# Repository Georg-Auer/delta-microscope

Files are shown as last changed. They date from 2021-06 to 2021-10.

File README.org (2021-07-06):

* Low-cost, automated microscope stage
* PureData Version
*This page describes how to build an automated inverted 3d printed microscope for observing microfluidics chips.*

This is a [[https://www.plus.ac.at/biowissenschaften/der-fachbereich/arbeitsgruppen/lepperdinger/spoc-labs/][SPOC lab]] project. Original source code of the project
is provided under MIT License. The source may contain code under a different license, if this is the case it is stated in the LICENSE file.
*This page describes how to create a simple het cam robot.*

If not stated otherwise, the designs and documentation in this repository
are made publicly available under a
[[https://creativecommons.org/licenses/by/4.0/][Creative Commons Attribution 4.0 International (CC BY 4.0)]] License.

#+CAPTION: Image of the 3D-printed version of the microscope.
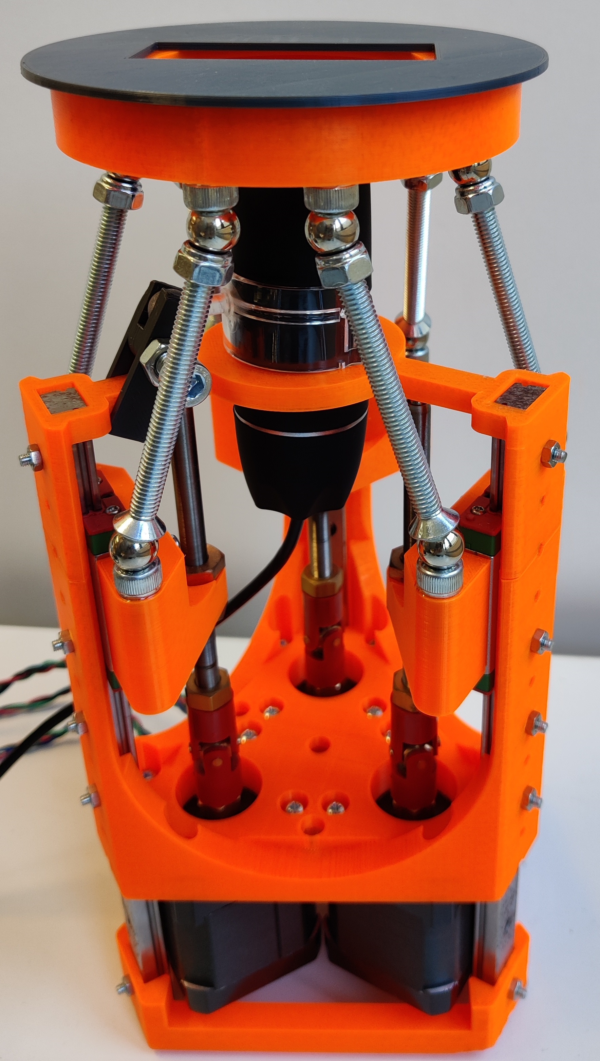
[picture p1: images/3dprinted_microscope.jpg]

#+BEGIN_QUOTE
Image of the 3D-printed microscope.
#+END_QUOTE

** Introduction

The microscope is designed to be as cheap and quick to manufacture as possible,
and still achieve high accuracy. Due to the chosen delta kinematics
the device has a very small footprint, and is also suitable for use in an incubator.
incubator. In the SPOC lab, the microscope is used
to observe and monitor the generation of spheroids in self-constructed chips and monitor the process.
The microscope can be controlled directly
or automated via a program to observe an experiment over time.

** Mechanics - Files and Bill of Materials   

*** Pump Design files (openSCAD)

The microscope model was designed in openSCAD in parametric form.
For each part, an stl file was created and all files where then sliced
with Prusa Slicer and sent to print on an 3D filament printer (Prusa MK3).
For the ease of reproduction of the slicer files are also saved within the directory.

#+CAPTION: A screenshot of the microscope in openSCAD.
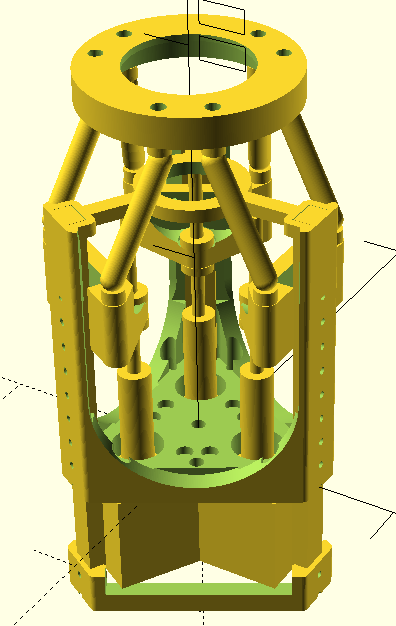
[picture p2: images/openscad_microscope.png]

#+BEGIN_QUOTE
A screenshot of the microscope in openSCAD (for the file see
[[./files/3d/openscad-microscope.scad]]).
#+END_QUOTE

*** Bill of Materials

| item                                                           | number | purpose               | bought from   |  part-no | costs in € |
|----------------------------------------------------------------+--------+-----------------------+---------------+----------+------------|
| Allegro A4983 Based Stepper Boards: here the 'Big Easy Driver' |      3 | stepper board         | Technobots    | 2900-445 | ~ 70       |
| Teensy 4.0 or 4.1 Microcontroller                              |      1 | stepper control       | Conrad        |  2269230 | ~ 30       |
| Nema 17 Steppers (0.9° 2.4 A)                                  |      3 | stepper motor         | Act-motor     | 1402-050 | ~ 60       |
| Fine Hex Adjuster, 1/4"-80, 4" Long                            |      3 | leadscrew             | Thorlabs      | F25SS400 | ~ 40       |
| Locking Phosphor-Bronze Bushing with Nut, 1/4"-80, L=0.50"     |      3 | leadscrewnut          | Thorlabs      |   N80L6P | ~ 28       |
| Linear Guide Rails (min 200 mm)                                |      3 | slides platform       | Amazon        | CNBTR214 | ~ 45       |
| Universal Coupling Body                                        |      3 | motor-screw-connector | Technobots    | 4604-050 | ~ 12       |
| Universal Coupling Insert - 5 mm                               |      3 | motor-side            | Technobots    | 4604-059 | ~ 8        |
| Universal Coupling Insert - 1/4"                               |      3 | screw-side            | Technobots    | 4604-066 | ~ 8        |
| OTHER SMALL ITEMS                                              |        |                       |               |          |            |
| 160 mm x 100 mm Copper Clad Stripboard                         |      1 | mount for electronics | Conrad        |          | ~ 2        |
| Male & Female PCB Headers 2.45 mm pitch                        |   some | simple connectors     | Conrad        |          | ~ 10       |
| Screws M3 (10 mm): 12 for motors, 6 for sliders, 15 for guides |     33 | mount slider & motors | Bauhaus       |          |            |
| Nuts M3                                                        |     33 | fixing screws         | Bauhaus       |          |            |
| Screws M6 (15 mm)                                              |     12 | suspension            | Bauhaus       |          |            |
| Screws M6 (60 mm)                                              |      6 | suspension            | Bauhaus       |          |            |
| Nuts M6 (end nut)                                              |      6 | suspension            | Bauhaus       |          |            |
| Neodymium bullet magnets ⌀ 10 mm                               |      6 | suspension            | Bauhaus       |          |            |
| USB (micro) cable                                              |      1 |                       | Conrad        |          | ~ 3        |
| 6 wire colored ribbon cable                                    |    3 m |                       | Conrad        |          | ~ 3        |
| 12 V / >=5 A power supply                                      |      1 |                       | Conrad        |          | ~ 20       |
| 197 g 3D-printer filament (PLA 1.75 mm)                        |1*250 g | microscope structure  | 3d jake       |          | ~ 10       |
| USA Digital Microscope 40x-1000x                               |      1 | microscope camera     | Bysameyee     |          | ~ 20       |
|----------------------------------------------------------------+--------+-----------------------+---------------+----------+------------|
|                                                                |        |                       |               |          | <  400     |

**** Companies:
- Technobots:  http://www.technobotsonline.com
- Thorlabs:    http:/www.thorlabs.com
- CPC-Farnell: http://cpc.farnell.com/
- RS:          http://uk.rs-online.com/web/
- Techsoft:    http://www.techsoft.co.uk/
- Maplin:      http://www.maplin.co.uk

All components but the optics-screws (Thorlabs) can be obtained
commercially. If other leadscrews are used, the software has to be
adapted to the distance/revolution grading.

**** Machines (and/or):
- FDM 3D-printer (we use an Prusa MK3, but any model with an similar precision would do)
#+EMAIL:  science@georgauer.com

#+CAPTION: Image of the 3D-printed version of robot.

#+BEGIN_QUOTE
Image of the robot.
#+END_QUOTE

** Introduction

Biocompatibility is of new untested materials is an important field.
This robot is a proposal of an automated het-cam experiment.

** TODO Mechanics - Files and Bill of Materials   

*** TODO  Design files

*** TODO Bill of Materials

- PLA
- stepper motor driver
- stepper motor
- arduino
- raspberry 4
- raspberry hq video camera

**** Machines (and/or):
- FDM 3D-printer (Prusa MK3, but any model with an similar precision would do)

**** Tools:
- Soldering iron
- Hand tools (screwdrivers etc.)

** Mechanical Assembly 

**** Pre-Assembly of Parts
***** Motor Part
- tin the leads of the motors with solder, add a male
  PCB-connector (or any other connector of your choosing. On our
  motors the colored leads are GREEN, BLACK, BLUE, RED).
- we use heatshrinking tube to electrically isolate the connectors at the end.
- add the connector for the leadscrew (5 mm brass insert) to the
  motor - you might not have space to do that later.

***** Leadscrew Part
- add the brass insert to connect the motor onto the leadscrew
- insert the screw VERY carefully to avoid damaging the thread which can
  happen rather easily.

***** Camera
The Microscope can be exchanged with an variety of solutions. We tried an Raspberry HQ Camera v1.0
with SM1 to C-mount adapter (thorlabs, SM1A9) to 1 inch optics connected to an Zeiss Plan 2,5 objective,
but eventually ended up with an 25€ USB microscope camera that has a 40x-1000x zoom option for maximal flexibility.

**** Assembly of the microscope

The STL files for the microscope where sliced in Prusa Slicer 2.2.0 and printed in ecoPLA NeonOrange with 20% infill.
The linear guide rails where screwed onto the main part, and the top part was then screwed onto the guide rails with 15xM3 screws and nuts.
For correct assembly, the top part has to end on height of the guide rails.
The three stepper motors where then screwed (12xM3) onto the bottom part.
The bottom part needs to be screwed on the other end of the guide rails (3xM3).
Now the universal couplings are screwed onto the motors and the optical fine threaded rods are fixed on the other side of the universal couplings.
For better durability, the plastic part of the universal couplings are glued to the metallic part with epoxy glue.
Six M6x15 mm screws are glued into the three slider parts, and M6x15 mm are glued into the platform as preparation for the magnetic joints.
The slider parts are now joined with their threaded insert and can be screwed onto the guide rails.
The end nuts are now placed on the M6 screws (60 mm) and the microscope stage is completed by putting the neodymium magnets in the joint positions.
Finally, the microscope-camera can be put in the ring on top where it is held in position with the printed clamp.

** Electronics
To drive the stepper motors we use a A4983 stepper driver
chip from Allegro Microsystems (datasheet http://www.technobotsonline.com/Datasheets2/1518-009-A4983SETTR-T.pdf).
For convenience we use one 'Big Easy Driver' for each motor
(http://www.technobotsonline.com/big-easy-driver.html,
http://www.schmalzhaus.com/BigEasyDriver/). The 'Big Easy Driver'
boards are nice, because they default to 16 step microstepping mode,
when the 'MS1, MS2, MS3' pins are left unconnected (which means that
less soldering has to be done). With 16-step microstepping, one
revelation of the leadscrew (318 micrometer movement) is divided into
400*16=6400 steps resulting in a stable flow even at very low
flowrates. The stepper drivers are controlled
with a teensy 4.0 or 4.1 microcontroller.

#+CAPTION: Left: Images of the electronics board with three stepper driver boards mounted. Right: Schematic diagram.

#+BEGIN_QUOTE
Left: Images of the electronics board with three stepper driver boards
mounted. Right: Schematic diagram.
#+END_QUOTE

*** Make the board
- solder connectors onto the driver board (e.g. PCB-connectors)

- layout the parts on a stripboard and drill holes so that you can
  mount the board with screws to an enclosure (e.g. from laser-cut
  acrylic).

- solder female PCB-connectors on the board for the teensy and the
  stepper boards (don't forget to cut the traces on the stripboard
  underneath).
- make all the necessary connections (see layout...)

- we made the system as simple as possible: 
  - no connection to MS1, MS2, MS3 - all are pulled high when not
    connected (means the driver defaults to 16 microstep-mode
  - no connection to sleep (slp) and reset (rst) - if powered the
    system will be on all the time. If you want to shut down the
    motors, turn off the power.
 
  - this leaves only the following connections to be made:
    - enable (en) is pulled low on all by connecting to ground (this
      is important, else the pins float).
    - shared GND between teensy and the quadstepper board (or single
      big easy drivers)
    - step-pin (stp): if high for >1 microsecond, the motor will step
    - direction-pin (dir): high/low sets the direction (if one of the motors
      steps the 'wrong' direction, just reverse the connections of the
      leads from (e.g. green, black, blue, red --> to red, blue,
      black, green).

  - Teensy is powered by a USB connection and the motors are powered
    separately (we use a 12V 5A power supply).

- Don't forget to adjust the current supplied to the motor with the
  small potentiometer on the stepper driver board. On max, the chip
  gets hot and the motor might have enough torque to continue beyond
  the end-stop, damaging the microscope assembly.

* Software for the Microscope
** Introduction - mode of operation and choice of tools

The microscope motors are controlled with a microcontroller (a 'teensy' 4.0 or 4.1)
and a software front end written in Pure Data (PD). The teensy
(https://www.pjrc.com/teensy/teensy31.html) is a 3.3V, 32-bit ARM
based microcontroller that is compatible with the Arduino toolchain
(https://www.arduino.cc/en/Guide/HomePage) and therefore easy to
program. The prime reason to use a teensy is the high speed USB data
transfer they allow
(https://www.pjrc.com/teensy/benchmark_usb_serial_receive.html). Apart
from controlling machinery, the teensy is well suited for data
acquisition tasks.

Pure Data (PD, https://puredata.info/) is an open source dataflow
programming language used primarily for music and video applications.
It runs on nearly every computing platform, is straightforward to
learn and can be modified 'live'.

The communication protocol between the microcontroller and PD is OSC
('Open Sound Control', https://www.opensoundcontrol.org). It is a very
flexible, easy to use two-way communication.

#+CAPTION: System diagram.

#+BEGIN_QUOTE
System diagram.
#+END_QUOTE

** Install the Software Toolchain
*** Arduino/Teensyduino
The easiest way to program teensy microcontrollers is to use the
Arduino IDE (download:https://www.arduino.cc/en/Main/Software). For
the teensy microcontrollers to be recognised by the Arduino IDE, one
must additionally install 'Teensyduino' (download:
https://www.pjrc.com/teensy/td_download.html). There is a detailed
tutorial on software installation and its use on the webpage. Most of
the Arduino libraries are compatible with teensy, Teensyduino itself
comes with many optimized ones (full install recommended).

** Setting up the System 
- program the teensy
- open the webpage

** How the System Works  
In the frontend control on the webpage, the rotation movement of the individual
of the individual motors is calculated.
This number of steps is now sent to the microcontroller,
which in turn controls the motor driver via the Step/Dir protocol.

** Getting it to Run
*** To get a debian system to run all necessary programs, use the new-raspi.sh shell script.

#+CAPTION: Screenshot of the program. 
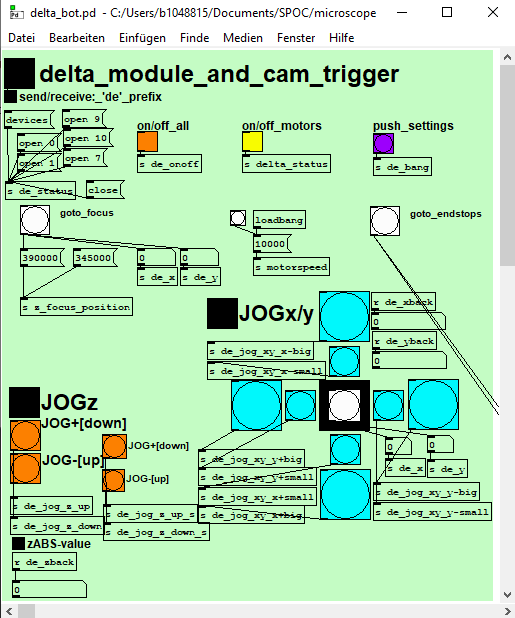
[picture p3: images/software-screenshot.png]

#+BEGIN_QUOTE
Screenshot of the program. 
#+END_QUOTE

- Hit [devices], and the available serial ports will show in the
  console window. One of them is connected to the teensy. Click [open
  x[ (change the numbers by entering editing mode, ctrl-e (linux),
  cmd-e (mac)) and PD should connect to the teensy.

- upload the corresponding file to the microcontroller
  ([[./files/delta_microscope_arduino/delta_microscope_arduino.ino]]).
- place the PD-programs ([[./files/delta_microscope/delta_microscope.pd]])
 together with a little helper-program for OSC ([[./files/o.io.slipserial.pd]]) in a folder and
  open it in PD-extended or PD-L2ORK.
- The file 'run.py' is the python/flask software.
- The files ([[./files/python/calibration.py]]) and ([[./files/frontend/delta_microscope_pd_osc_receiver.pd]])
  can be used together to calibrate the microscope.

#+CAPTION: Screenshot of the program. 
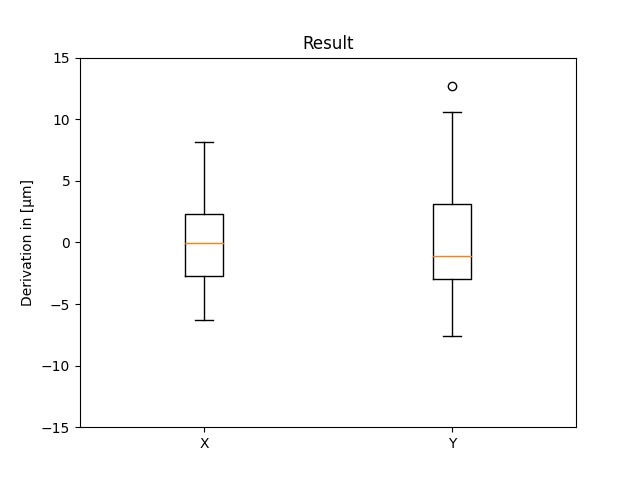
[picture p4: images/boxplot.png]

#+BEGIN_QUOTE
The microscope stage can now be controlled via an additional python script.
At first, an experiment to run to different x/y positions and back to the origin has to be created and executed.
After reaching the origin again, a picture of a raster is taken and saved in the experiment folder.

After running the experiment 25 times (n = 25), this resulting boxplot was calculated automatically with the calibration.py script.
#+END_QUOTE
** TODO Assembly

* Software for the Microscope
** TODO Introduction 

git clone --recurse-submodules git@github.com:spoc-lab/delta-microscope.git

pip install -r requirements.txt
for torch on armv7l:
https://github.com/Kashu7100/pytorch-armv7l

# install torch on Raspberry 3/4:
sudo apt install libopenblas-dev libblas-dev m4 cmake cython python3-dev python3-yaml python3-setuptools
cd ~/Downloads
git clone https://github.com/Kashu7100/pytorch-armv7l.git
cd pytorch-armv7l/
sudo pip3 install torch-1.7.0a0-cp37-cp37m-linux_armv7l.whl
sudo pip3 install torchvision-0.8.0a0+45f960c-cp37-cp37m-linux_armv7l.whl

# install on all systems:
sudo pip3 install -r requirements.txt

How to make the script run on startup:
sudo nano /etc/rc.local
insert:
cd home/pi/het-cam-dashboard
sudo CAMERA=opencv python3 run.py &

# git pull on startup
sudo nano ~/.profile
git --git-dir=/delta-microscope/.git pull main

or for additional logging:
sudo CAMERA=opencv python3 run.py & > /home/pi/Desktop/log.txt 2>&1

https://blog.miguelgrinberg.com/post/flask-video-streaming-revisited

to start an OpenCV session from bash, you can do this:

$ CAMERA=opencv python3 run.py

From a Windows command prompt you can do the same as follows:

on windows run:
$ python run.py CAMERA=opencv
$ py -3.7 run.py CAMERA=opencv

or:
$ set CAMERA=opencv
$ python run.py
$ py -3.7 run.py

or on linux with gunicorn:
# gunicorn -b 127.0.0.1:8080 app:app
# gunicorn -w 2 -b 127.0.0.1:8080 app:app

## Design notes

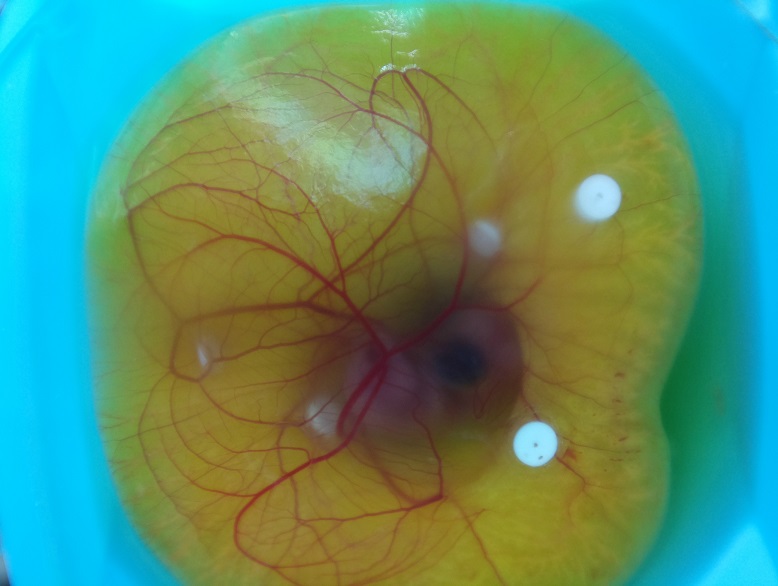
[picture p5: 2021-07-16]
het-cam-ha-small.jpg

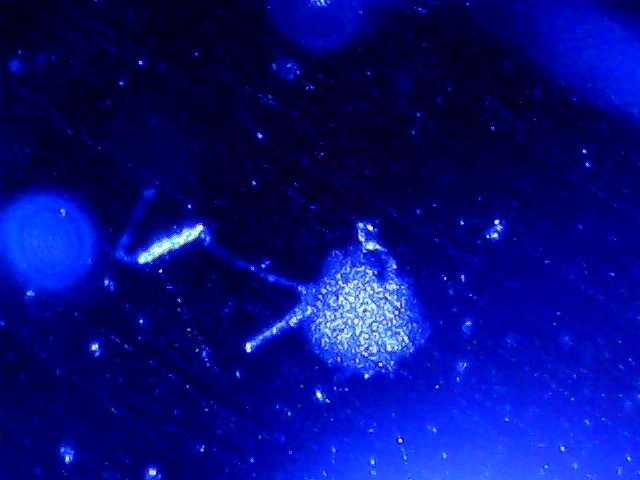
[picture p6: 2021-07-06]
spheroids1.jpg

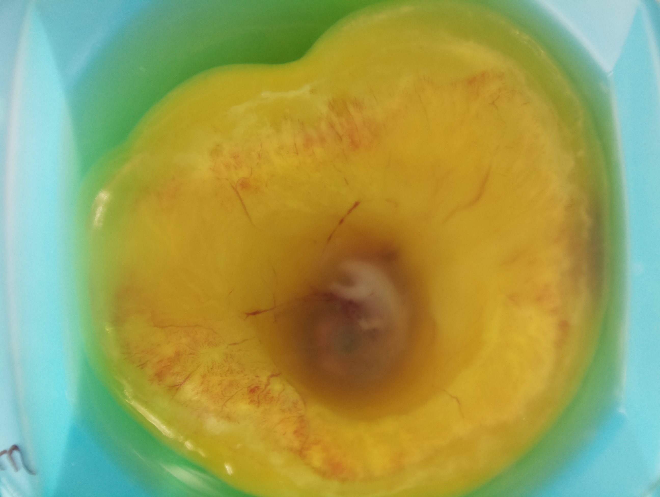
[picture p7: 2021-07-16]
het-cam-dead.jpg

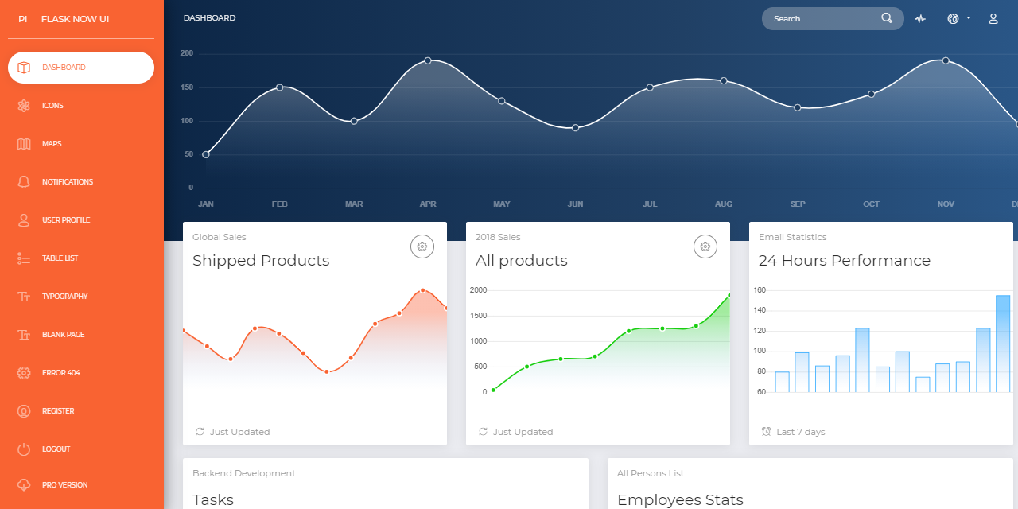
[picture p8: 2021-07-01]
media/flask-now-ui-dashboard-screen.png

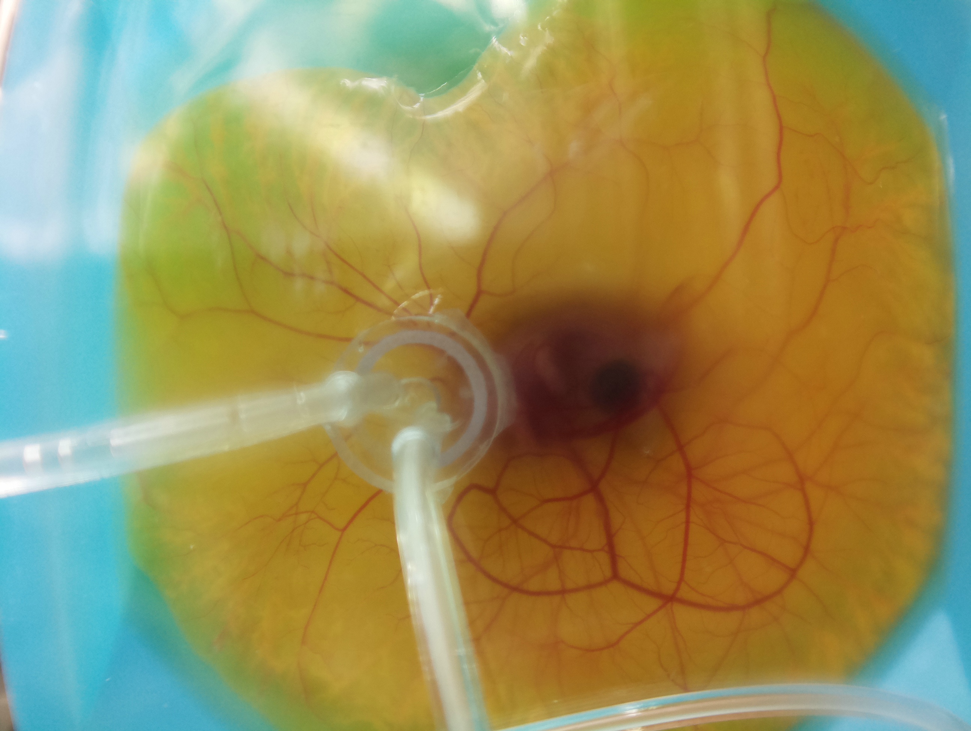
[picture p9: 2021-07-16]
het-cam.jpg

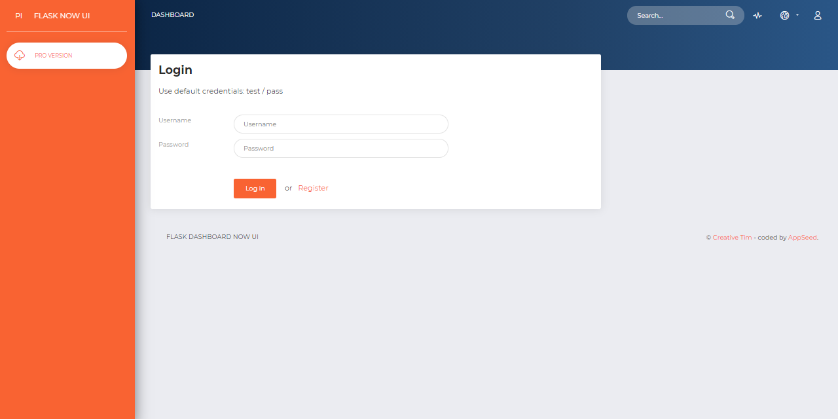
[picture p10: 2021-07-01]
media/flask-now-ui-dashboard-screen-login.png

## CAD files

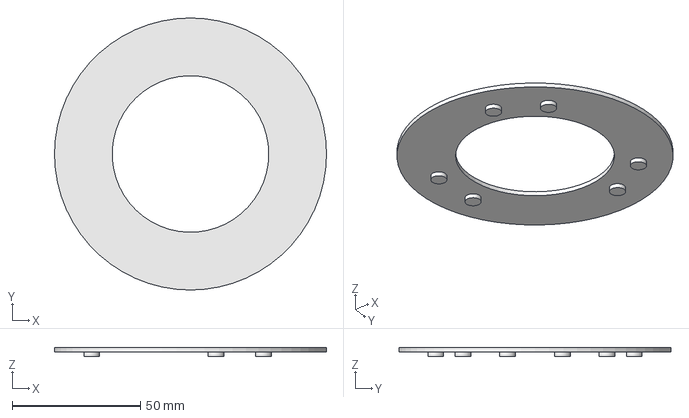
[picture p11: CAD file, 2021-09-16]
files/3d/accessories/complete_cutout_turntable_accessory.step
106.0 x 106.0 x 3.50 mm

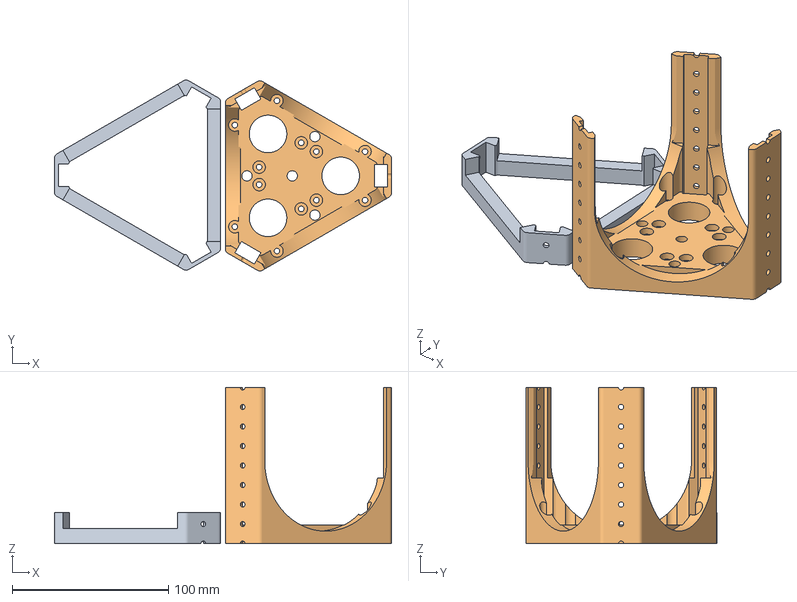
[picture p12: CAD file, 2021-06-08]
files/3d/mainparts_0.2mm_tolerance.3mf
215.7 x 122.3 x 100.0 mm
bottompart_delta_0.2mm_tolerance.stl
mainpart_delta_0.2mm_tolerance.stl

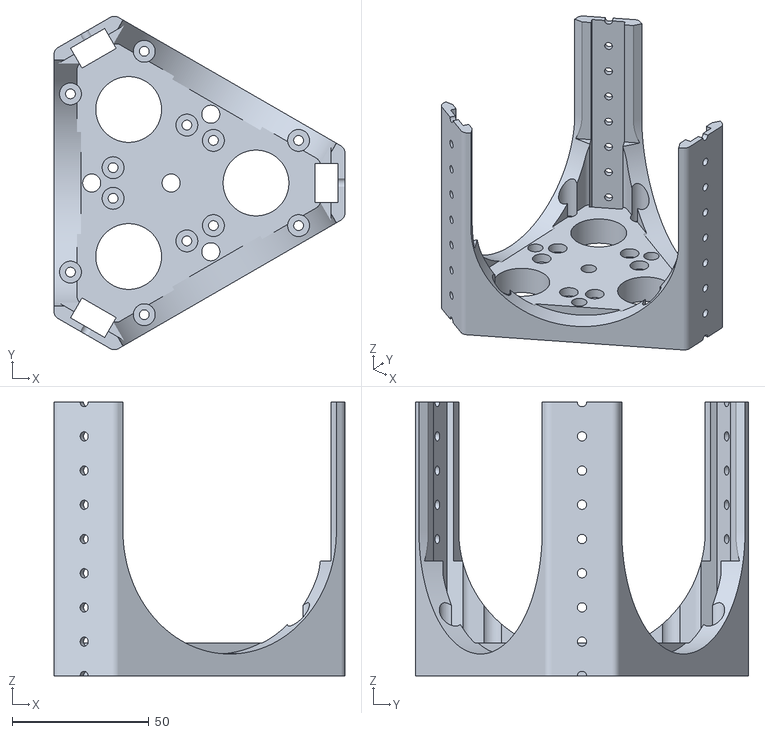
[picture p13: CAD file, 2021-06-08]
files/3d/mainpart_delta_0.2mm_tolerance.stl
106.3 x 121.8 x 100.0

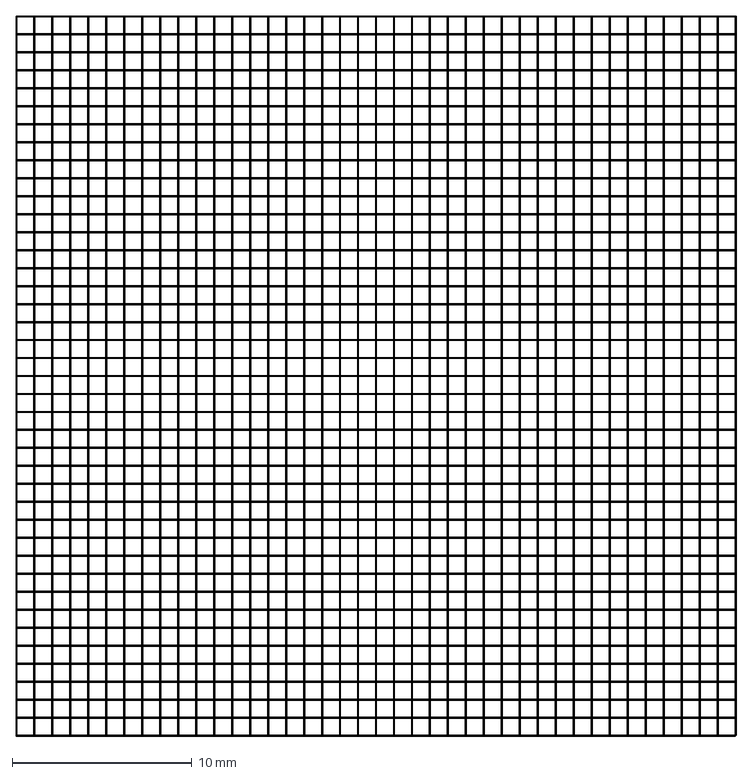
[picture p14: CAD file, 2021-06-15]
files/calibration/raster4x4.dxf
40.0 x 40.0 mm

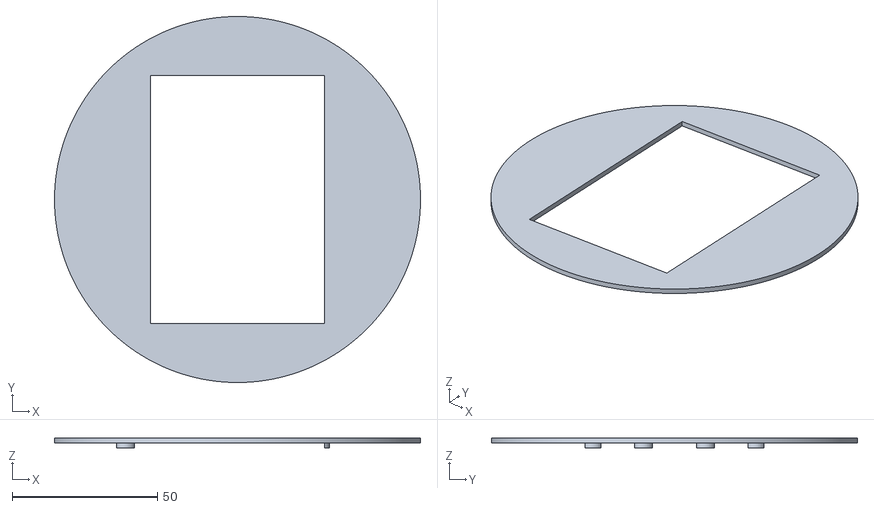
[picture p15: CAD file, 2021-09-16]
files/3d/accessories/modified_turntable_accessory_incubationchamber_85x59.4stl.stl
126.0 x 126.0 x 3.50

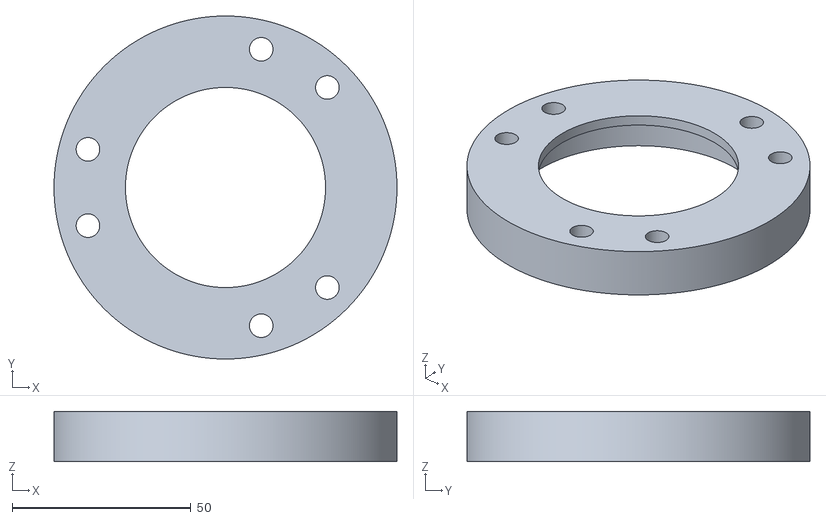
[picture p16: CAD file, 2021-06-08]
files/3d/platform_delta_0.2mm_tolerance.stl
96.0 x 96.0 x 14.0

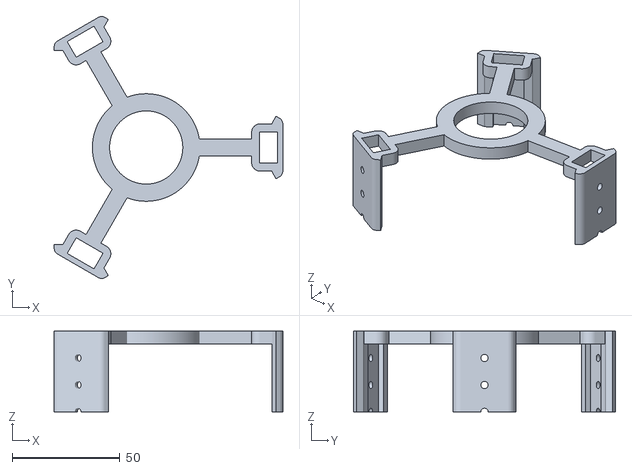
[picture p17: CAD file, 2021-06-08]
files/3d/toppart_delta_0.2mm_tolerance.stl
106.3 x 121.8 x 37.5

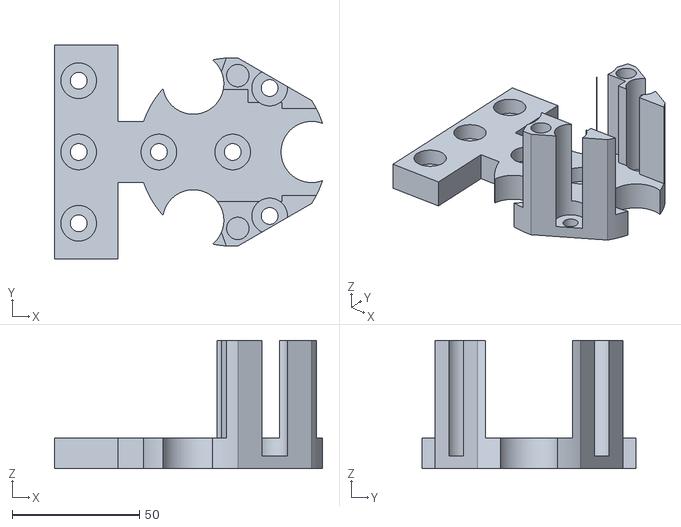
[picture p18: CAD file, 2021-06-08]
files/3d/optics_delta_0.2mm_tolerance.stl
105.3 x 84.0 x 50.3

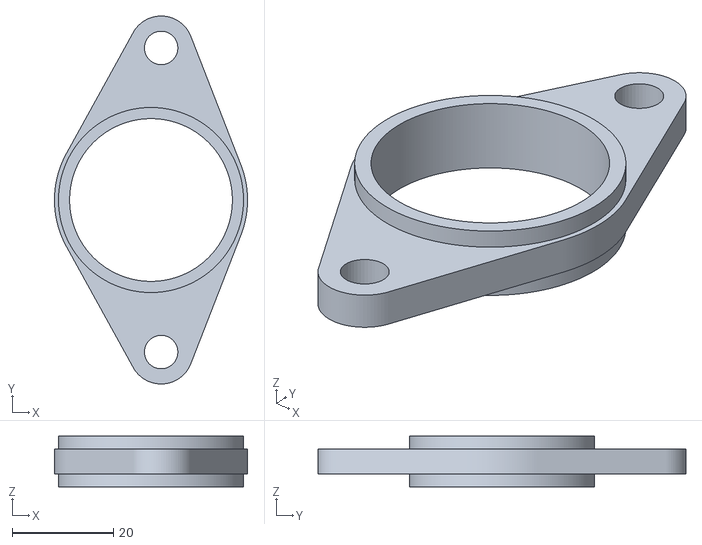
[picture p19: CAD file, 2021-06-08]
files/3d/optics_fixture_delta_0.2mm_tolerance.stl
38.1 x 72.6 x 10.0

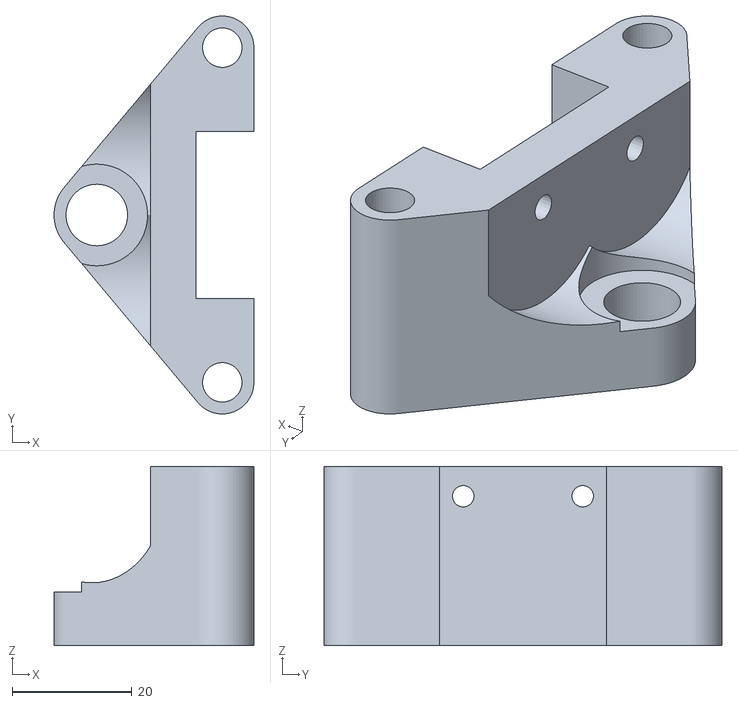
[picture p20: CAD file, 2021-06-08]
files/3d/slider_x3_delta_0.2mm_tolerance.stl
33.4 x 66.6 x 30.0

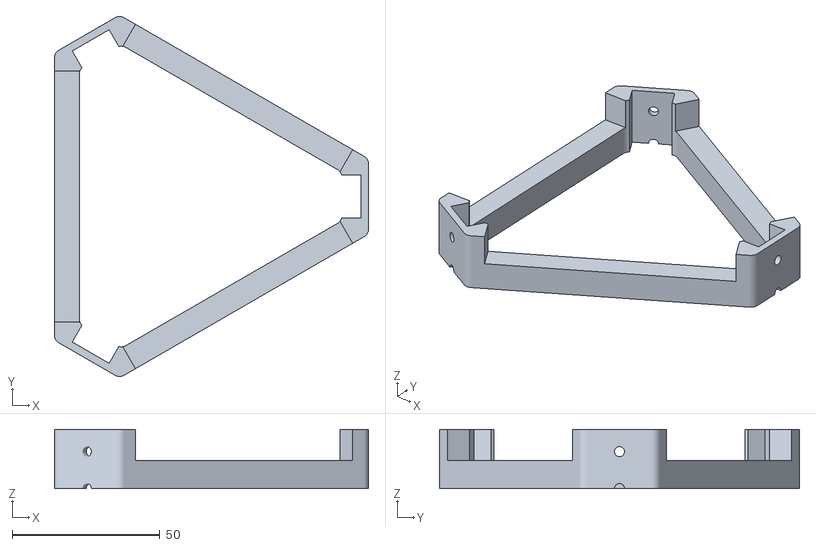
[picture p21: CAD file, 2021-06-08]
files/3d/bottompart_delta_0.2mm_tolerance.stl
106.3 x 121.8 x 20.0

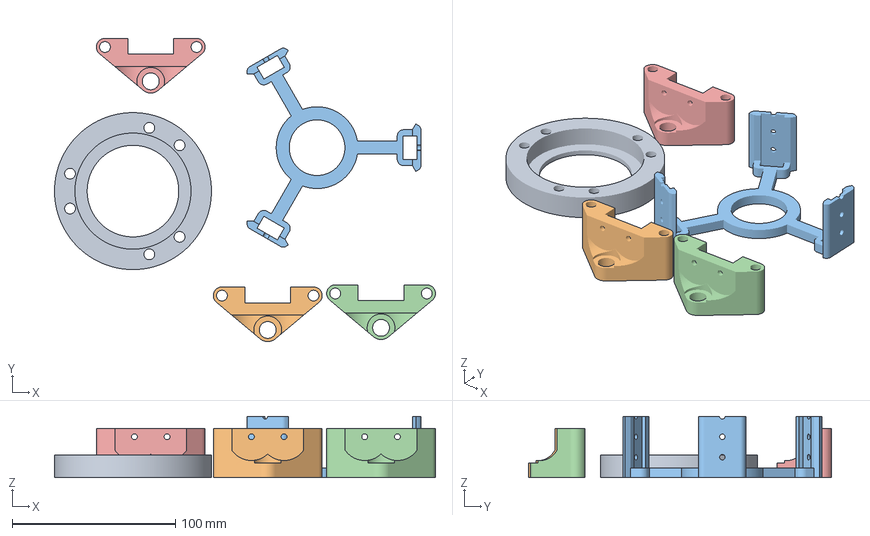
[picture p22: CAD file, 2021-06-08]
files/3d/small_parts_0.2mm_tolerance.3mf
233.0 x 185.5 x 37.5 mm
platform_delta_0.2mm_tolerance.stl
slider_x3_delta_0.2mm_tolerance.stl x 3
toppart_delta_0.2mm_tolerance.stl

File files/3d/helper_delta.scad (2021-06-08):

//mini nema17-based delta
//printable on 120x120x120 trinus - max size possible
//and pumps to mount onto the scaffold
//===================================================

tolerance=0.2; //added tolerance at places needed to make 3d-printed part fit

//==================
//variables baseunit
//==================
base_r=31;//this is where the center-motorhole is located from abs center; adjusts size in xy; 31=min for nema17; this keeps all 'inside features' while making it easy to adjust outside wall via 'movewallfrombase_r'
movewallfrombase_r=29.5; //this variable moves the outside wall further from base_r (center motor holes)
height_all=100; //=height of delta-part
platethickness=12;//thickness of baseplate
reinforcementheight=30;//height above plate where hiwin-carriage is not cut out from wall
edge_y_distance=22; //distance of cylinders to form hull (inside-wall=edge_y_distance-wallthickness); use this variable to adjust wall behind sliders
wallthickness=9;//thickness of wall (grows to the inside)
edge_r=3;//'roundness' of edges
//M6 centerholes made so that hex-head is embedded
M6baseholes_r=3.3; //size of hole in center
M6_sinking_depth=7;//depth of access holes for M6 screws so that hex-head or nut is fully sunk
M6baseholeaccess_r=7;

motor_screw_diagonal = 44;//to mount nema17's 
middlemotor_r = 12; //radius of middle 'hole' of motors, big enough for 3d-printed couplers
M3_r=1.8;//a bit r added for not too tight holes to mount motors
motorscrews_access_r=4; //access_r for motor screws
motorscrews_access_heightbelowbaseplate=4; //how deep access holes go into baseplate
//subtract cylindrical shape from walls
//------------------------------------
cylinder_dia=45;
cylinder_length=100; //just that it easy to hit the wall for subtraction
wallheight_hole=-4;//mm above bottomplate where cylindrical cutout starts
cutout_r=33;//where from center cutout in wall will start
///variables hiwin
//----------------
M4_r=1.7; //r for screws, unfortunately imperial, therefore M3 screws must be used
M4_distance=12.5; //distance mounting holes, twice as many holes than in slider (25mm distance)
M4length=22; //length of screws
slide_width=14;//hiwin-slide=12mm +2mm space on each side
slide_thickness=8;//thickness hiwin-slide

slide_length=200;//length of hiwin-slides
move_slide_from_Zzero=-62.5; //move slider + screws above/below z-zero
slider_distance=22; //additional distance of slider from 'base-radius' base_r; take care if motors interfere
hiwin_carrierheight=5; //height of slider vs rail of hiwin from above
hiwin_carrier_width=28; //width of hiwin carrier (27mm+1)      
hiwin_carrier_thickness=10; //   

//===============
//variables TOP-Deltapart
//===============
delta_toplength=60;
delta_topwidth=20;
delta_topthickness=6;
delta_top_hole_r=17;
delta_top_wallthickness=8;

//=====================
//variables for slider
//=====================
height_slider = 80;//this defines where (height above plate) carriage is 
sliderwall=2;//thickness of wall around vertical holes
sliderpart_z_height=30;//height in z     
magnetdistance_to_sides=56; //USE THIS TO MAXIMISE MOVEMENT POSSIBLE + s_holder_r_in & s_holder_M6_r
magnetdistance_from_base_r=21; //distance in x from base_r to magnets   
M6_r=3.3; //+0.3 for 3d-printing

M6magnet_cutout_dia=6;//can put magnets lower, now commented out
M6magnet_cutout_height=7;//can put magnets lower, now commented out


bolt_distance_carrier=20; //distance holes on hiwin slider
carrier_screwlength=20;
screw_lengthinplastic=8;
sliderscrewaccess_r=3;
sliderscrewaccess_r_top=14.5;//r of cutout on top-screws connected on hiwin carrier

leadscrewnut_accessdia = 8.5; //leadscrewnut-nuts r=7.5 'leadscrewnut_top_bottom_r'

//========================
//variables for base plate
//========================
height_all_bottompart=20; //=height of delta-bottom_part
wallheight_hole_bottompart=5;//mm above bottomplate where cylindrical cutout starts
cylinder_dia_bottompart=60;
bottompart_base_correction=-8;//arbitrary value to adjust height of connection piece

//=======================================
//variables for drawing mechanical parts
//=======================================
//draw motors
motor_length = 48;
motor_width = 42;
motor_halfdiagonal = 0.5* sqrt(2*(motor_width*motor_width)); //half the diagonal of square area of motor, could be too big when edges of motor are rounded
//draw shafts, coupler, leadscrew and leadscrewnut
shaftcoupler_length = 52;//the usual red one
shaftcoupler_radius = 7.5;//the usual red one

leadscrew_length = 130; //~4" +approx height of shaft-coupler=42
leadscrew_radius = 3.05;
//dimensions thorlabs-nut
leadscrewnut_length = 9;
leadscrewnut_minradius = 5.15; //dia real = 9.5, 0.3mm tolerance added for 3d-printing
leadscrewnut_top_bottom_r=7.5;
leadscrewnut_top_bottom_thickness=4;
//=====================================

//==========================
//variables optics parts
//==========================

//point grey fireflyMV camera
//===========================
//main body
ptgrey_x=44;
ptgrey_y=34;
ptgrey_z=19.18;
//USB-port
ptgrey_x_USB=10; //check with caliper
ptgrey_y_USB=15; //check with caliper
ptgrey_z_USB=5.2;
//IO-port
ptgrey_x_IO=15; //check with caliper
ptgrey_y_IO=5; //check with caliper
ptgrey_z_IO=2; //too much, but like this easy to see...
IO_from_left_edge=33.49;
IO_from_top_edge=7.56;
//============================


//30mm-thorlabs-cage (e.g. mirror)
//================================
cageoptics_xy=38.3+2*tolerance;
cageoptics_z=38.3;
itemonside_xy=12;
itemonside_thickness=5+tolerance;
itemonfront_thickness=20;//takes away space for 1inch optics
itemonfront_width=34;//takes away space for 1inch optics  

//thorlabs c->1" adapter
c_to_1inch_adapter_r_outer=15.35;
c_to_1inch_adapter_r_inner=11.45;
c_to_1inch_adapter_height=4.4; 
// 1" optics tubes
tube1inch_outer_r=15.25;
tube1inch_inner_r=11.45;
// tube1
t1_tube1inch_length=80;
//tube2
t2_tube1inch_length=25.4;
//10xolympus_objective
olympus10x_parfocal_length=45.06;
olympus10x_parfocal_r=0.5;
olympus10x_body1_r=12; 
olympus10x_bodylength1=28;
olympus10x_body2_r=8;
olympus10x_bodylength2=32;
olympus10x_body3_r=5.25;
olympus10x_bodylength3=34;
//==============================
//variables optics ground plate
//=============================
//round part
optics_plate_r=37;//adjust this to fit well inside deltapart
optics_plate_z=12; //z-height of plate
optics_plate_z_high=optics_plate_z+cageoptics_z; //z-height of middle part
opticsplate_fixhole_r=29;

//brass-inserts to mount fixture
 M6insert_r=4.4;//4.5 good for holes across layers, but too big when holes are in other printing direction
 M6insert_height=14; //min 13.5mm
 insert_x=2;
 insert_y=30;
//connector-part to outside
optics_addpart1_x=15;//must be larger than wall-end of deltapart
optics_addpart1_y=24;//must fit to size of corresponding cylinder-cutout from deltapart 
optics_addpart_movex=30;//moves connector part in x, make it fit to the optics plate in delta
//outside part which serves to screw on bigger outside platform
optics_addpart2_x=25;
optics_addpart2_y=84;  

//=============================
//optics-plate - fixture on top
//=============================
opticsfixture_height=5;
opticsfixture_wallsize=3;
//====================
//optics ADDED plate
//====================
opticsaddedplate_x=87.5;
opticsaddedplate_y=112.5;  
holestepsize=12.5;


//==================================
//PLATFORM (slide-holder)-variables
//==================================
s_holder_height=14;
s_holder_r_out=48;
// MAX MOVEMENT ADJUSTMENT: s_holder_r_in & s_holder_M6_r & magnetdistance_to_sides
s_holder_r_in=35.5;//ADJUST THIS TO MAXIMISE MOVEMENT "when the objective crushes into platform" 
//to find best place for screws and the dimensions of the place iterate manually until both ECHO messages (or green and yellow inner circles match and are at max
s_holder_M6_r=28.5; //ADJUST THIS TO MAXIMISE MOVEMENT "where the hex-screws are" 
s_holder_FOV_r_outside=base_r+magnetdistance_from_base_r-s_holder_M6_r; //base for ECHO: diameter of movement possible from outside structure (one side: rods vertical)
s_holder_FOV_r_inside=s_holder_r_in-olympus10x_body1_r; //base for ECHO: diameter of movement possible from inside structure (ring and objective) 

s_holder_r_top=28;  //s_holder_r_in; //only needed to differ from s_holder_r_in if uscope slide is to small... 
s_holder_r_top_height=3;//holding structure smaller than air-gap between objective and sample

//carriage-platform connectors
//============================   
     magnet_r=5;//neodymium sphere radius
     hex_r=4.95;//hex-head_r 
     hex_height=5.85;//hex-head height
     magnet_in_hex_height=9.9;//measure this: when magnet is assembled in hex, where is its center, if hexhead-'bottom' = 0?
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

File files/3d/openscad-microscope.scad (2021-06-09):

//mini nema17-based delta
//printable on 120x120x120 trinus - max size possible
//and pumps to mount onto the scaffold
//===================================================

tolerance=0.2; //added tolerance at places needed to make 3d-printed part fit

//==================
//variables baseunit
//==================
base_r=31;//this is where the center-motorhole is located from abs center; adjusts size in xy; 31=min for nema17; this keeps all 'inside features' while making it easy to adjust outside wall via 'movewallfrombase_r'
movewallfrombase_r=29.5; //this variable moves the outside wall further from base_r (center motor holes)
height_all=100; //=height of delta-part
platethickness=12;//thickness of baseplate
reinforcementheight=30;//height above plate where hiwin-carriage is not cut out from wall
edge_y_distance=22; //distance of cylinders to form hull (inside-wall=edge_y_distance-wallthickness); use this variable to adjust wall behind sliders
wallthickness=9;//thickness of wall (grows to the inside)
edge_r=3;//'roundness' of edges
//M6 centerholes made so that hex-head is embedded
M6baseholes_r=3.3; //size of hole in center
M6_sinking_depth=7;//depth of access holes for M6 screws so that hex-head or nut is fully sunk
M6baseholeaccess_r=7;

motor_screw_diagonal = 44;//to mount nema17's 
middlemotor_r = 12; //radius of middle 'hole' of motors, big enough for 3d-printed couplers
M3_r=1.8;//a bit r added for not too tight holes to mount motors
motorscrews_access_r=4; //access_r for motor screws
motorscrews_access_heightbelowbaseplate=4; //how deep access holes go into baseplate
//subtract cylindrical shape from walls
//------------------------------------
cylinder_dia=45;
cylinder_length=100; //just that it easy to hit the wall for subtraction
wallheight_hole=-4;//mm above bottomplate where cylindrical cutout starts
cutout_r=33;//where from center cutout in wall will start
///variables hiwin
//----------------
M4_r=1.7; //r for screws, unfortunately imperial, therefore M3 screws must be used
M4_distance=12.5; //distance mounting holes, twice as many holes than in slider (25mm distance)
M4length=22; //length of screws
slide_width=14;//hiwin-slide=12mm +2mm space on each side
slide_thickness=8;//thickness hiwin-slide

slide_length=200;//length of hiwin-slides
move_slide_from_Zzero=-62.5; //move slider + screws above/below z-zero
slider_distance=22; //additional distance of slider from 'base-radius' base_r; take care if motors interfere
hiwin_carrierheight=5; //height of slider vs rail of hiwin from above
hiwin_carrier_width=28; //width of hiwin carrier (27mm+1)      
hiwin_carrier_thickness=10; //   

//===============
//variables TOP-Deltapart
//===============
delta_toplength=60;
delta_topwidth=20;
delta_topthickness=6;
delta_top_hole_r=17;
delta_top_wallthickness=8;

//=====================
//variables for slider
//=====================
height_slider = 80;//this defines where (height above plate) carriage is 
sliderwall=2;//thickness of wall around vertical holes
sliderpart_z_height=30;//height in z     
magnetdistance_to_sides=56; //USE THIS TO MAXIMISE MOVEMENT POSSIBLE + s_holder_r_in & s_holder_M6_r
magnetdistance_from_base_r=21; //distance in x from base_r to magnets   
M6_r=3.3; //+0.3 for 3d-printing

M6magnet_cutout_dia=6;//can put magnets lower, now commented out
M6magnet_cutout_height=7;//can put magnets lower, now commented out


bolt_distance_carrier=20; //distance holes on hiwin slider
carrier_screwlength=20;
screw_lengthinplastic=8;
sliderscrewaccess_r=3;
sliderscrewaccess_r_top=14.5;//r of cutout on top-screws connected on hiwin carrier

leadscrewnut_accessdia = 8.5; //leadscrewnut-nuts r=7.5 'leadscrewnut_top_bottom_r'

//========================
//variables for base plate
//========================
height_all_bottompart=20; //=height of delta-bottom_part
wallheight_hole_bottompart=5;//mm above bottomplate where cylindrical cutout starts
cylinder_dia_bottompart=60;
bottompart_base_correction=-8;//arbitrary value to adjust height of connection piece

//=======================================
//variables for drawing mechanical parts
//=======================================
//draw motors
motor_length = 48;
motor_width = 42;
motor_halfdiagonal = 0.5* sqrt(2*(motor_width*motor_width)); //half the diagonal of square area of motor, could be too big when edges of motor are rounded
//draw shafts, coupler, leadscrew and leadscrewnut
shaftcoupler_length = 52;//the usual red one
shaftcoupler_radius = 7.5;//the usual red one

leadscrew_length = 130; //~4" +approx height of shaft-coupler=42
leadscrew_radius = 3.05;
//dimensions thorlabs-nut
leadscrewnut_length = 9;
leadscrewnut_minradius = 5.15; //dia real = 9.5, 0.3mm tolerance added for 3d-printing
leadscrewnut_top_bottom_r=7.5;
leadscrewnut_top_bottom_thickness=4;
//=====================================

//==========================
//variables optics parts
//==========================

//point grey fireflyMV camera
//===========================
//main body
ptgrey_x=44;
ptgrey_y=34;
ptgrey_z=19.18;
//USB-port
ptgrey_x_USB=10; //check with caliper
ptgrey_y_USB=15; //check with caliper
ptgrey_z_USB=5.2;
//IO-port
ptgrey_x_IO=15; //check with caliper
ptgrey_y_IO=5; //check with caliper
ptgrey_z_IO=2; //too much, but like this easy to see...
IO_from_left_edge=33.49;
IO_from_top_edge=7.56;
//============================


//30mm-thorlabs-cage (e.g. mirror)
//================================
cageoptics_xy=38.3+2*tolerance;
cageoptics_z=38.3;
itemonside_xy=12;
itemonside_thickness=5+tolerance;
itemonfront_thickness=20;//takes away space for 1inch optics
itemonfront_width=34;//takes away space for 1inch optics  

//thorlabs c->1" adapter
c_to_1inch_adapter_r_outer=15.35;
c_to_1inch_adapter_r_inner=11.45;
c_to_1inch_adapter_height=4.4; 
// 1" optics tubes
tube1inch_outer_r=15.25;
tube1inch_inner_r=11.45;
// tube1
t1_tube1inch_length=80;
//tube2
t2_tube1inch_length=25.4;
//10xolympus_objective
olympus10x_parfocal_length=45.06;
olympus10x_parfocal_r=0.5;
olympus10x_body1_r=12; 
olympus10x_bodylength1=28;
olympus10x_body2_r=8;
olympus10x_bodylength2=32;
olympus10x_body3_r=5.25;
olympus10x_bodylength3=34;
//==============================
//variables optics ground plate
//=============================
//round part
optics_plate_r=37;//adjust this to fit well inside deltapart
optics_plate_z=12; //z-height of plate
optics_plate_z_high=optics_plate_z+cageoptics_z; //z-height of middle part
opticsplate_fixhole_r=29;

//brass-inserts to mount fixture
 M6insert_r=4.4;//4.5 good for holes across layers, but too big when holes are in other printing direction
 M6insert_height=14; //min 13.5mm
 insert_x=2;
 insert_y=30;
//connector-part to outside
optics_addpart1_x=15;//must be larger than wall-end of deltapart
optics_addpart1_y=24;//must fit to size of corresponding cylinder-cutout from deltapart 
optics_addpart_movex=30;//moves connector part in x, make it fit to the optics plate in delta
//outside part which serves to screw on bigger outside platform
optics_addpart2_x=25;
optics_addpart2_y=84;  

//=============================
//optics-plate - fixture on top
//=============================
opticsfixture_height=5;
opticsfixture_wallsize=3;
//====================
//optics ADDED plate
//====================
opticsaddedplate_x=87.5;
opticsaddedplate_y=112.5;  
holestepsize=12.5;


//==================================
//PLATFORM (slide-holder)-variables
//==================================
s_holder_height=14;
s_holder_r_out=48;
// MAX MOVEMENT ADJUSTMENT: s_holder_r_in & s_holder_M6_r & magnetdistance_to_sides
s_holder_r_in=35.5;//ADJUST THIS TO MAXIMISE MOVEMENT "when the objective crushes into platform" 
//to find best place for screws and the dimensions of the place iterate manually until both ECHO messages (or green and yellow inner circles match and are at max
s_holder_M6_r=28.5; //ADJUST THIS TO MAXIMISE MOVEMENT "where the hex-screws are" 
s_holder_FOV_r_outside=base_r+magnetdistance_from_base_r-s_holder_M6_r; //base for ECHO: diameter of movement possible from outside structure (one side: rods vertical)
s_holder_FOV_r_inside=s_holder_r_in-olympus10x_body1_r; //base for ECHO: diameter of movement possible from inside structure (ring and objective) 

s_holder_r_top=28;  //s_holder_r_in; //only needed to differ from s_holder_r_in if uscope slide is to small... 
s_holder_r_top_height=3;//holding structure smaller than air-gap between objective and sample

//carriage-platform connectors
//============================   
     magnet_r=5;//neodymium sphere radius
     hex_r=4.95;//hex-head_r 
     hex_height=5.85;//hex-head height
     magnet_in_hex_height=9.9;//measure this: when magnet is assembled in hex, where is its center, if hexhead-'bottom' = 0?
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

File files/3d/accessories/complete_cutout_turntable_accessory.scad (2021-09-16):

magnetdistance_to_sides=56; //USE THIS TO MAXIMISE MOVEMENT POSSIBLE + s_holder_r_in & s_holder_M6_r
magnetdistance_from_base_r=21; //distance in x from base_r to magnets   
M6_r=3.3; //+0.3 for 3d-printing

M6magnet_cutout_dia=6;//can put magnets lower, now commented out
M6magnet_cutout_height=7;//can put magnets lower, now commented out

s_holder_r_top=28;  //s_holder_r_in; //only needed to differ from s_holder_r_in if uscope slide is to small... 
s_holder_r_top_height=3;//holding structure smaller than air-gap between objective and sample

s_holder_height=14;
s_holder_r_out=48;
// MAX MOVEMENT ADJUSTMENT: s_holder_r_in & s_holder_M6_r & magnetdistance_to_sides
s_holder_r_in=35.5;//ADJUST THIS TO MAXIMISE MOVEMENT "when the objective crushes into platform" 
//to find best place for screws and the dimensions of the place iterate manually until both ECHO messages (or green and yellow inner circles match and are at max
s_holder_M6_r=28.5; //ADJUST THIS TO MAXIMISE MOVEMENT "where the hex-screws are" 

/*
//make cylindical platform
difference (){
cylinder(r = s_holder_r_out, h = s_holder_height, $fa=1, $fs=0.5);
cylinder(r = s_holder_r_in, h = s_holder_height-s_holder_r_top_height, $fa=1, $fs=0.5);
cylinder(r = s_holder_r_top, h = s_holder_height, $fa=1, $fs=0.5);  

for(turn0 = [0 : 120 : 360])
rotate([0,0,turn0]){
//attachment M6+magnets    
translate ([s_holder_M6_r, -magnetdistance_to_sides/2,0])  
cylinder(r = M6_r, h = s_holder_height, $fa=1, $fs=0.5);
translate ([s_holder_M6_r, magnetdistance_to_sides/2,0])  
cylinder(r = M6_r, h = s_holder_height, $fa=1, $fs=0.5);
}
}

*/

//tolerance due to fff printing method
tolerance = 0.2;
slide_tolerance = 0.1;

//to avoid the need for supports during printing:
slide_holder_overhang = 5;

//size of an typical slide
single_slide_lenght_1 = 76+tolerance;
single_slide_lenght_2 = 75+tolerance;
single_slide_width_1 = 26+tolerance;
single_slide_width_2 = 25+tolerance;

ring_widening = 5;

//create slide holding platform
color("red"){
translate ([0,0,20]){
difference(){

union(){



for(turn0 = [0 : 120 : 360])
rotate([0,0,turn0]){
//attachment poles    
translate ([s_holder_M6_r, -magnetdistance_to_sides/2,0])
cylinder(r = M6_r-tolerance, h = s_holder_height/8, $fa=1, $fs=0.5);
translate ([s_holder_M6_r, magnetdistance_to_sides/2,0])  
cylinder(r = M6_r-tolerance, h = s_holder_height/8, $fa=1, $fs=0.5);
}
translate ([0,0,s_holder_height/8])

//platform
difference(){
cylinder(r = s_holder_r_out+ring_widening, h = s_holder_height/8, $fa=1, $fs=0.5);
cylinder(r = s_holder_r_in, h = s_holder_height-s_holder_r_top_height, $fa=1, $fs=0.5);
cylinder(r = s_holder_r_top, h = s_holder_height, $fa=1, $fs=0.5);




}
}//end of union

// single slide frame
rotate([0,0,15]){
cube(size = [single_slide_lenght_1,single_slide_width_1,s_holder_height], center = true);
}
rotate([0,0,-15]){
cube(size = [single_slide_lenght_2,single_slide_width_2,s_holder_height], center = true);
}
// double slide frame
cube(size = [single_slide_width_1*2+slide_tolerance,single_slide_lenght_1+slide_tolerance,s_holder_height], center = true);
}
}
}

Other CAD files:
files/3d/accessories/modified_turntable_accessory_incubationchamber.scad
files/3d/accessories/complete_cutout_turntable_accessory.stl

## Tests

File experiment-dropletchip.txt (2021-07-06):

[0, 0, 0]
[100000, -50000, 0]
[20000, -170000, -40000]
[-100000, -110000, -40000]
[-160000, -220000, -110000]
[-40000, -270000, -110000]
[-120000, -360000, -150000]
[-280000, -390000, -180000]
[-170000, -430000, -180000]
[-230000, -500000, -210000]
[-330000, -450000, -210000]
[-360000, -510000, -220000]
[-410000, -560000, -240000]
[-320000, -600000, -240000]

'0,0,0\r\n100000, -50000, 0\r\n20000, -170000, -40000\r\n-100000, -110000, -40000\r\n-160000, -220000, -110000\r\n-40000, -270000, -110000\r\n-120000, -360000, -150000\r\n-280000, -390000, -180000\r\n-170000, -430000, -180000\r\n-230000, -500000, -210000\r\n-330000, -450000, -210000\r\n-360000, -510000, -220000\r\n-410000, -560000, -240000\r\n-320000, -600000, -240000'

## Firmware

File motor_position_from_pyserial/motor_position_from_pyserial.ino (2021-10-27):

#include <AccelStepper.h>
// https://www.pjrc.com/teensy/td_libs_AccelStepper.html
//configure AccelStepper to mode 1 (Step/Dir)
int board1 = 1;
//define Pins
int motor0_en = 1;
int motor0_dir = 2;
int motor0_step = 3;

int motor1_en = 4;
int motor1_dir = 5;
int motor1_step = 6;

int motor2_en = 7;
int motor2_dir = 8;
int motor2_step = 9;

int motor3_en = 10;
int motor3_dir = 11;
int motor3_step = 12;

//define Pins on AccelStepper library
AccelStepper motor0(board1, motor0_step, motor0_dir);
AccelStepper motor1(board1, motor1_step, motor1_dir);
AccelStepper motor2(board1, motor2_step, motor2_dir);
AccelStepper motor3(board1, motor3_step, motor3_dir);//...(1[means driver board], step, dir)

struct STRUCT {
  int motor0_enable = 1;
  int motor0_direction;
  int motor0_position;
  int motor0_speed = 5000;
  int motor1_enable = 1;
  int motor1_direction;
  int motor1_position;
  int motor1_speed = 5000;
  int motor2_enable = 1;
  int motor2_direction;
  int motor2_position;
  int motor2_speed = 5000;
  int motor3_enable = 1;
  int motor3_direction;
  int motor3_position;
  int motor3_speed = 5000;
} testStruct;

#include "SerialTransfer.h"

int ledPin = 13;     // pin that the led is attached to
//int analogvalue = 0;
int32_t arduino_motorA = 0;
int32_t arduino_motorB = 0;
int32_t arduino_motorC = 0;

int calculate_motorA(int32_t x_movement, int32_t y_movement, int32_t z_movement){
  //calculate arduino_motor A,B,C here
  int delta_arms = 1214550;  // L=60.12mm 1step = 0.0495um =1214550 ticks
  //int delta_radius = ????;
  int Ax0 = 408178; //=Bx0
  int Ay0 = 235663; //=By0
  arduino_motorA = (sqrt((pow(delta_arms,2))-(pow((Ax0+x_movement),2))-(pow((Ay0+y_movement),2))))-z_movement-0.5; //-0.5 to round down!
  int start_value = 1119367;
  arduino_motorA = arduino_motorA-start_value;
  return (arduino_motorA);
}
int calculate_motorB(int32_t x_movement, int32_t y_movement, int32_t z_movement){
  //calculate arduino_motor A,B,C here
  int delta_arms = 1214550;  // L=60.12mm 1step = 0.0495um =1214550 ticks
  //int delta_radius = ????;
  int Ax0 = 408178; //=Bx0
  int Ay0 = 235663; //=By0
  arduino_motorB = (sqrt(pow(delta_arms,2)-(pow((Ax0-x_movement),2))-(pow((Ay0+y_movement),2))))-z_movement-0.5; //-0.5 to round down!
  int start_value = 1119367;
  arduino_motorB = arduino_motorB-start_value;
  return (arduino_motorB);
}
int calculate_motorC(int32_t x_movement, int32_t y_movement, int32_t z_movement){
  //calculate arduino_motor A,B,C here
  int delta_arms = 1214550;  // L=60.12mm 1step = 0.0495um =1214550 ticks
  //int delta_radius = ????;
  int Cy0 = 471323;
  arduino_motorC = (sqrt((pow(delta_arms,2))-(pow(x_movement,2))-(pow((Cy0-y_movement),2))))-z_movement-0.5; //-0.5 to round down!
  int start_value = 1119368;
  arduino_motorC = arduino_motorC-start_value;
  return (arduino_motorC);
}
SerialTransfer myTransfer;

void setup()  
  {       
  
  //TODO: enable/disable motors from python
  
  //enable motors
  pinMode (motor0_en, OUTPUT); //motor0_EN
  pinMode (motor1_en, OUTPUT); //motor1_EN
  pinMode (motor2_en, OUTPUT); //motor2_EN
  pinMode (motor3_en, OUTPUT); //motor3_EN
  //motors on/off
  digitalWrite (motor0_en, HIGH); //motor0 HIGH:off, LOW:on
  digitalWrite (motor1_en, HIGH); //motor1
  digitalWrite (motor2_en, HIGH); //motor2
  digitalWrite (motor3_en, HIGH); //motor3
  
  motor0.setMaxSpeed(20000);  //always necessary, default very slow
  motor1.setMaxSpeed(20000); 
  motor2.setMaxSpeed(20000);
  motor3.setMaxSpeed(20000); 
  
  Serial.begin(115200);
  myTransfer.begin(Serial);

  //for testing purposes
  pinMode(ledPin, OUTPUT);  //set switch as input pin for rawdata-mode
  digitalWrite (ledPin, LOW);
}

void loop()  
{

  if(myTransfer.available())
  {
    // find size of transferred message
    uint16_t recSize = 0;
    recSize = myTransfer.rxObj(testStruct, recSize);
    
    // do the enable here, otherwise the stop condition and the motorX_en interfere
    digitalWrite (motor0_en, testStruct.motor0_enable); //motor0
    digitalWrite (motor1_en, testStruct.motor1_enable); //motor1
    digitalWrite (motor2_en, testStruct.motor2_enable); //motor2
    digitalWrite (motor3_en, testStruct.motor3_enable); //motor3

    //delta mechanics calculation
    arduino_motorA = calculate_motorA(testStruct.motor0_position,testStruct.motor1_position,testStruct.motor2_position);
    arduino_motorB = calculate_motorB(testStruct.motor0_position,testStruct.motor1_position,testStruct.motor2_position);
    arduino_motorC = calculate_motorC(testStruct.motor0_position,testStruct.motor1_position,testStruct.motor2_position);
    
    // send all received data back to Python
    for(uint16_t i=0; i < myTransfer.bytesRead; i++)
      myTransfer.packet.txBuff[i] = myTransfer.packet.rxBuff[i];
    
    myTransfer.sendData(myTransfer.bytesRead);
  }

  // motor0.moveTo(testStruct.motor0_position);
  // motor1.moveTo(testStruct.motor1_position);
  // motor2.moveTo(testStruct.motor2_position);
  // motor3.moveTo(testStruct.motor3_position);

  motor0.moveTo(arduino_motorA);
  motor1.moveTo(arduino_motorB);
  motor2.moveTo(arduino_motorC);
  // motor3.moveTo(testStruct.motor3_position);

  motor0.setSpeed(testStruct.motor0_speed);
  motor1.setSpeed(testStruct.motor1_speed);
  motor2.setSpeed(testStruct.motor2_speed);
  motor3.setSpeed(testStruct.motor3_speed);

  motor0.runSpeedToPosition();  
  motor1.runSpeedToPosition();
  motor2.runSpeedToPosition();
  motor3.runSpeedToPosition();

// since the mechanics from each motor has a slight influence to all others
// the motors are only switched off if all movement is completed
// and every momentum (forward or backlash) is expected to be 0
  // if (motor0.distanceToGo()== 0 && motor1.distanceToGo()== 0 && motor2.distanceToGo()== 0 && motor3.distanceToGo()== 0){
  //   delay(300);
  //   digitalWrite (motor0_en, HIGH); //motor0
  //   testStruct.motor0_enable = 1; // turn motors off after distanceToGo is 0 for all motors
  //   digitalWrite (motor1_en, HIGH); //motor1
  //   testStruct.motor1_enable = 1;
  //   digitalWrite (motor2_en, HIGH); //motor2
  //   testStruct.motor2_enable = 1;
  //   digitalWrite (motor3_en, HIGH); //motor3
  //   testStruct.motor3_enable = 1;
  // }

  if (motor0.distanceToGo()== 0){
    // delay(500);
    digitalWrite (motor0_en, HIGH); //motor0
    testStruct.motor0_enable = 1; // turn motor off after distanceToGo is 0
  }
  if (motor1.distanceToGo()== 0){
    // delay(500);
    digitalWrite (motor1_en, HIGH); //motor1
    testStruct.motor1_enable = 1;
  }
  if (motor2.distanceToGo()== 0){
    // delay(500);
    digitalWrite (motor2_en, HIGH); //motor2
    testStruct.motor2_enable = 1;
  }
  if (motor3.distanceToGo()== 0){
    digitalWrite (motor3_en, HIGH); //motor3
    testStruct.motor3_enable = 1;
  } 
}  

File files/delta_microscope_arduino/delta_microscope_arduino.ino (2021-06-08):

//quadstepper_inverted deltabot

// kinematics integrated, 
// after movement finished, 
// cam and LED is triggered with time-settings specified in the OSC-message
// enable/disable motors

//xyz movement

//pins:
/*
-STANDARD WIRING DIAGRAM (teensy 3.x): not all pins are used in every setup!
=================================================================== 
    
* Modular Setup - PIN connections - teensy 3.2/3.6 compatible

| PIN | PUMP           | Pump-function  | DELTA-BOT      | SOLENOIDS | Sol-driver | MEASUREMENT/SORTING     | M/S function                                                             |
|-----+----------------+----------------+----------------+-----------+------------+-------------------------+--------------------------------------------------------------------------|
|   0 |                |                |                | SOL1      | ULN1/Pin1  |                         |                                                                          |
|   1 | enablePumppin  | EnableP0       | ENMD1          | SOL2      | ULN1/Pin2  |                         |                                                                          |
|   2 | directionpin   | DIRpump0       | MD1            | SOL3      | ULN1/Pin3  |                         |                                                                          |
|   3 | steppin        | STEPpump0      | MD1            | SOL4      | ULN1/Pin4  |                         |                                                                          |
|   4 | enablePump1pin | EnableP1       | ENMD2          | SOL5      | ULN1/Pin5  |                         |                                                                          |
|   5 | directionpin1  | DIRpump1       | MD2            | SOL6      | ULN1/Pin6  |                         |                                                                          |
|   6 | steppin1       | STEPpump1      | MD2            | SOL7      | ULN1/Pin7  |                         |                                                                          |
|   7 | enablePump2pin | EnableP2       | ENMD3          | SOL8      | ULN1/Pin8  |                         |                                                                          |
|   8 | directionpin2  | DIRpump2       | MD3            |           |            |                         |                                                                          |
|   9 | steppin2       | STEPpump2      | MD3            |           |            |                         |                                                                          |
|  10 | enablePump3pin | EnableP3       | not used       |           |            |                         |                                                                          |
|  11 | directionpin3  | DIRpump3       | not used       |           |            |                         |                                                                          |
|  12 | steppin3       | STEPpump3      | not used       |           |            |                         |                                                                          |
|-----+----------------+----------------+----------------+-----------+------------+-------------------------+--------------------------------------------------------------------------|
|  13 | not used       | not used       | not used       | SOL16     | ULN2/Pin8  |                         |                                                                          |
|  14 | A0 (not used)  | Trigger (opt)  | A0=cam-trigger | SOL15     | ULN2/Pin7  |                         |                                                                          |
|  15 | A1 (not used)  | Trigger (opt)  | A1=LED-trigger | SOL14     | ULN2/Pin6  |                         |                                                                          |
|  16 | endStopFpin    | EndSTOPP0Front | ESTOPMD1F      | SOL13     | ULN2/Pin5  |                         |                                                                          |
|  17 | endStopBpin    | EndSTOPP0Back  | ESTOPMD1B      | SOL12     | ULN2/Pin4  |                         |                                                                          |
|  18 | endStop1Fpin   | EndSTOPP1Front | ESTOPMD2F      | SOL11     | ULN2/Pin3  | Trigger3                | broken out with GND                                                      |
|  19 | endStop1Bpin   | EndSTOPP1Back  | ESTOPMD2B      | SOL10     | ULN2/Pin2  | Trigger2                | broken out with GND                                                      |
|  20 | endStop2Fpin   | EndSTOPP2Front | ESTOPMD3F      | SOL9      | ULN2/Pin1  | Trigger1                | broken out with GND                                                      |
|  21 | endStop2Bpin   | EndSTOPP2Back  | ESTOPMD3B      |           |            | CAMERA-Trigger          | broken out with GND                                                      |
|  22 | endStop3Fpin   | EndSTOPP3Front | not used       |           |            | LED-Strobe-Trigger      | broken out with GND                                                      |
|  23 | endStop3Bpin   | EndSTOPP3Back  | not used       |           |            | SENSOR-Measurement (A9) | with Analog-GND + 3.3V (talos-sensors); A-GND only (BNC-connected sens.) |
|     |                |                |                |           |            |                         |                                                                          |



camera-trigger: pin 14
LED-trigger: pin 15


motor1 (towerA, MD1)
enable              1
DIR                 2
STP                 3

motor2 (towerB, MD2)
enable              4
DIR                 5
STP                 6

motor3 (towerC, MD3)
enable              7
DIR                 8
STP                 9


Big Easy Driver - things not used:
/////////////////////////////////////////////////////////////////////////////////////
MS1 MS2 MS3  (16 ustepping per default)
H   H   H    1/16
/////////////////////////////////////////////////////////////////////////////////////

FORMAT OF THE OSC_MESSAGE
/////////////////////////
position/speed motors; 
camera-waiting time after movement completed (usec); 
3x(strobepulse & duration - in usec after camera was triggered); 
CAM&LED-on/off 

17 values:
==========

in_motorA
speed_motorA
in_motorB
speed_motorB
in_motorC
speed_motorC

delta_status
*/

// Library for stepper motors
#include <AccelStepper.h>

//define Pins
AccelStepper motorA(1, 3, 2);
AccelStepper motorB(1, 6, 5);
AccelStepper motorC(1, 9, 8);//...(1[means driver board is used], step, dir)

///libraries and code for OSC communication
#include <OSCBundle.h>
#include <OSCBoards.h>

#ifdef BOARD_HAS_USB_SERIAL
#include <SLIPEncodedUSBSerial.h>
SLIPEncodedUSBSerial SLIPSerial( thisBoardsSerialUSB );
#else
#include <SLIPEncodedSerial.h>
SLIPEncodedSerial SLIPSerial(Serial);
#endif

//OSC

// Read new position - incoming from PD, seems unused and should be removed
int32_t in_motorA = 0;
int32_t in_motorB = 0;
int32_t in_motorC = 0;

// used for endstops and start-stop
int delta_status = 0;

//-----------------------new for internal coordinates
//internal motor Values
int32_t arduino_motorA = 0;
int32_t arduino_motorB = 0;
int32_t arduino_motorC = 0;

//internal x,y,z values
int32_t arduino_x = 0;
int32_t arduino_y = 0;
int32_t arduino_z = 0;
//------------------------------------

//which speed?
int32_t speed_motorA = 20000;
int32_t speed_motorB = 20000;
int32_t speed_motorC = 20000;
int32_t speed_motorABC = 20000;
int32_t endstopspeed = 15000; //steps/s and anti-clockwise movement if go to endstop is triggered

//raw-coordinates xyz (in ticks)
int x_movement = 0;
int y_movement = 0;
int z_movement = 0;

//int send = 0; //prints positions via OSC to periphery, print is 0 at start

const int ledPin = 13;  //for debugging
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

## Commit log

2021-06-08 adapt to delta microscope
    [171031_3D-printed_mini_nema17_all_0.2mmtolerance-noalpha.scad, 3DprintedSyringeAdaptors.scad, PumpPartsLaserCut.dxf, SyringePump3Dmodel.scad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]
2021-06-09 update doc
    [bottompart_delta_0.2mm_tolerance.stl, helper_delta.scad, mainpart_delta_0.2mm_tolerance.stl, mainparts_0.2mm_tolerance.3mf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]
2021-06-09 side syringe pumps removed
    [openscad-microscope.scad]
2021-06-09 version without pumps
2021-06-11 insert of missing names
2021-06-14 updates to doc
    [small_parts_0.2mm_tolerance-minimal-version.3mf, small_parts_0.2mm_tolerance.3mf]
2021-06-15 documentation additionals
    [raster4x4.dxf]
2021-06-21 python program included
    [raster4x4.dxf]
2021-06-22 calibration setup
2021-06-22 removed pre-assembly
2021-07-06 remove print
2021-07-16 yolo inference not working, testing het-cam weights
2021-07-20 new setup for 32 and 64bit raspberry os
2021-07-21 active status works now on camera-settings
2021-09-06 on offf led mode
2021-09-16 holder for incubation chamber
    [complete_cutout_turntable_accessory.scad, complete_cutout_turntable_accessory.step, complete_cutout_turntable_accessory.stl, modified_turntable_accessory_incub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]
2021-09-21 new led pin 18 (relais)
2021-09-21 led 18 off
2021-09-21 led on/off
2021-09-21 new experiment turns LED on
2021-09-21 standard led off
2021-09-21 led status change debug
2021-09-21 led in auto mode off
2021-09-22 led switch on/off on button press
2021-10-05 humidity temperature record via DHT22
2021-10-05 pin to self.pin
2021-10-05 set pin
2021-10-13 speed included in arduino and python
2021-10-13 arduino setup to v 1.8.16
2021-10-15 new arduino setup, needs more testing
2021-10-17 xywh result print
2021-10-19 2 sensor possible
2021-10-20 printing coordinates and confidence of yolo
2021-10-20 self.yolo_results print
2021-10-27 stopping motor only after all distances are 0
2021-10-27 switch off motors individually
2021-11-03 print detect parameters
2021-11-14 minor updates for raspberry os bullseye
2021-11-15 sensor set message
2021-11-26 log instead of print in run.py
2021-11-26 log enabled in experiments and camera module
